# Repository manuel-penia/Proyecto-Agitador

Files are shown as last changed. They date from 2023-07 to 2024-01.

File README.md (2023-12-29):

# Agitador Magnético

En este proyecto se documenta la realización de un agitador magnético sencillo de bajo costo y con **componentes reutilizados** de computadoras viejas. Incluimos los componentes y circuitos asi como del software usado para controlar, mediante una placa Arduino, la velocidad de giro de un ventilador y la actuación sobre una pantalla de 7 segmentos que muestra un temporizador.

---

# Contenidos

1. [Motivación](#Motivación)
    1. [¿Agitadores magnéticos?](##¿Agitadoresmagnéticos?)
2. [Nuestro Agitador](#NuestroAgitador)
    1. [Uso](#uso)
    2. [Lista de Componentes](#lista-de-componentes)
    3. [Circuito](#circuito)
    4. [Software](#software)
    5. [Impresión 3D](#Impresión3D)
3. [Inspiración](#Inpiración)

---

# Motivación

<p align="justify"> Realizamos este proyecto con el fin de crear una sistema de fácil implementación para construir un agitador magnético que actualmente tienen precios altos y que sea funcional para el trabajo en el laboratorio.
 </p>

## ¿Agitadores magnéticos?

<p align="justify"> Los agitadores magnéticos se utilizan para la mezclar de soluciones químicas. Los agitadores comerciales consisten de una pequeña barra magnética recubierta por una capa de plástico y una placa debajo donde se encuentra un imán rotatorio a fin de crear un campo magnético que gire. Es muy frecuente que tenga un montaje de resistencias eléctricas a fin de generar calor necesario para calentar algunas soluciones químicas.</p>
___

# Nuestro Agitador

<p align="justify"> Para el diseño de nuestro agitador tuvimos en cuenta que debía tener la funcionalidad principal de hacer girar el buzo (para realizar el mezclado) y a su vez que tuviera un temporizador, con el cual pasado el tiempo seleccionado se apague el agitador. </p>

## Uso

<p align="justify"> Presionando el botón amarillo se elige la cantidad de tiempo deseada en el temporizador, con el botón rojo se da inicio al descuento de dicho tiempo. Se puede frenar el giro del ventilador presionando nuevamente el botón rojo. Una vez que arrancó el temporizador, mediante el giro del potenciómetro se controla la velocidad de giro del ventilador y por ende del buzo en la solución. Recomendamos aumentar gradualmente la velocidad de giro hasta la velocidad deseada. 
 </p>

## Lista de componentes

1. [Placa Arduino UNO](https://proyectoarduino.com/arduino-uno-r3/)
2. Entradas:
    1. [Potenciómetro](https://programarfacil.com/blog/arduino-blog/el-potenciometro-y-arduino/)
    2. [Botones](https://openwebinars.net/blog/tutorial-arduino-entradas-2-botones/) .
3. Salidas:

    1. Ventilador con PWM [AMD AFB 3300 rpm](https://ar.mouser.com/datasheet/2/632/AFB70x70x15mm-515820.pdf)
    2. [Display LCD](https://www.circuitbasics.com/arduino-7-segment-display-tutorial/).

4. Alimentación:

    1. Fuente de aliemntacion 12 V [Megalite SF120050](https://megalite.com.ar/data/Catalogo_Nielsen.pdf).

5. Otros accesorios:
    1. Cables Dupont Macho Hembra y Macho Macho de 20cm x **30**.

## Circuito

<p align="justify"> En cuanto al circuito, la fuente de alimentación se conecta a la placa Arduino mediante la entrada de 12V. El pin Vin redirecciona el voltaje de alimentación al ventilador. A traves del relay se conecta el cable Vin que conecta el ventilador. El controlador PWM del ventilador sale del pin 3 que tiene funcionalidad PWM. Por otro lado, la salida analógica del potenciómetro se conecta al Arduino por la entrada A2 y la alimentación es de 5V que proporciona el Arduino. El modulo Relay tiene su sistema de de alimentación de 5V con los pines de la placa y el cable sensor por la salida digital 8. Ademas cuenta con 2 botones en una configuración pull-down. Para esto se conecta una resistencia de 10 ohms en la salida GND de los botones. Todos estos componentes se conectan a los pines GND del Arduino. Finalmente el display LCD 16 x 2  se conectan las entradas analogicas A5 y A4 como indica la imagen, estas funcionan como comunicación, luego la alimentación es por 5V propio del arduino. Todos los componentes deben conectarse a tierra. </p>

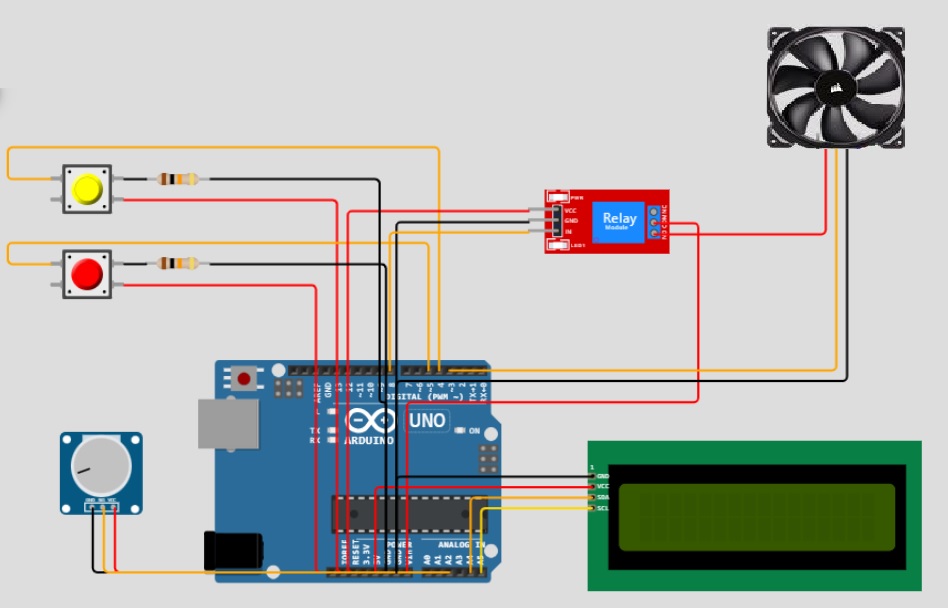
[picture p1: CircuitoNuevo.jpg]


## Software

El código utilizado se encuentra en el archivo [Codigo-Arduino.ino](https://github.com/manuel-penia/Proyecto-Agitador/blob/main/C%C3%B3digo-Arduino.ino)
Para simplificar la lectura y funcionamiento del codigo se realizo el siguiente diagrama explicativo. En donde, las variables azules son globales y las negras son locales.

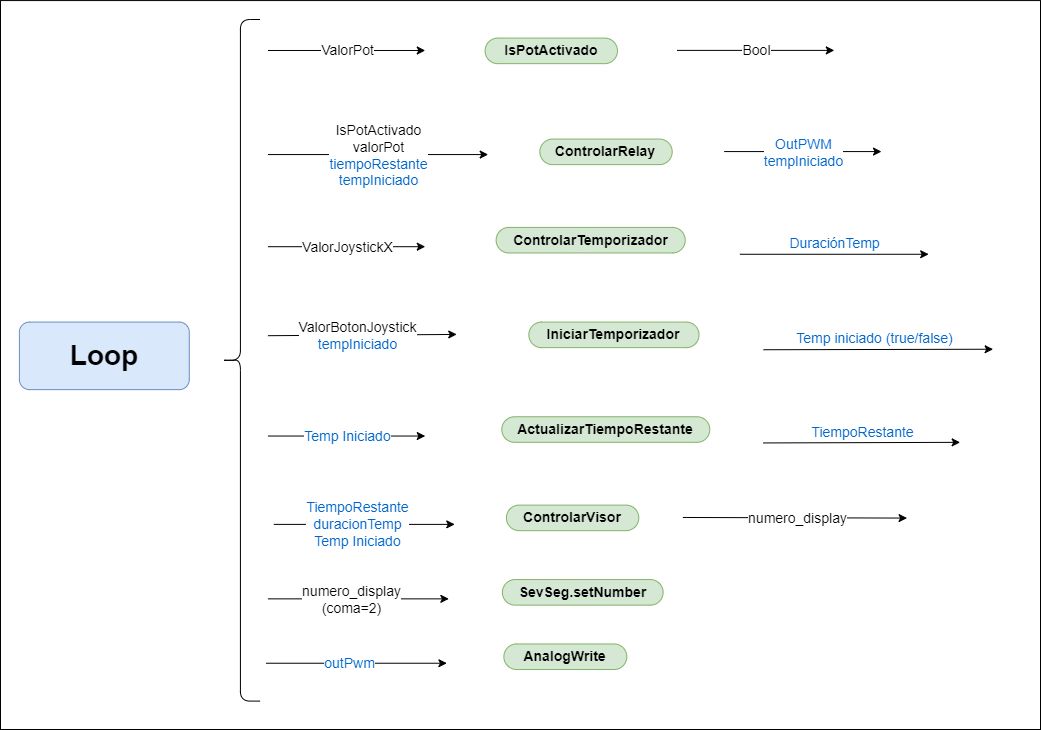
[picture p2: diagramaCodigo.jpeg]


## Impresión 3D

Se construyó un soporte en la plataforma online TinkerCad dispuesto en tres partes. El diseño consta de tres partes, la inferior, la intermedia y la superior. En la inferior hay espacios para atornillar la placa y el relé al suelo y contra una de las paredes se conectan los botones (Se construye una parte que funciona como traba), potenciometro y el visor LED. La intermedia se debe encastrar a la parte inferior y sobre ella se atornilla el ventilador con el imán pegado. La parte superior se desliza sobre las otras dos funcionando como tapa.
Para regular la fuerza de los imánes se construyó una plataforma circular que eleve el vaso precipitado a la distancia deseada.
También se contruyó el buzo que se introduce en la solución. Dentro del buzo se encuentran los imanes de neodimio. Todos los archivos stl se encuentran en esta [carpeta.](https://github.com/manuel-penia/Proyecto-Agitador/tree/main/IMPRESI%C3%93N)

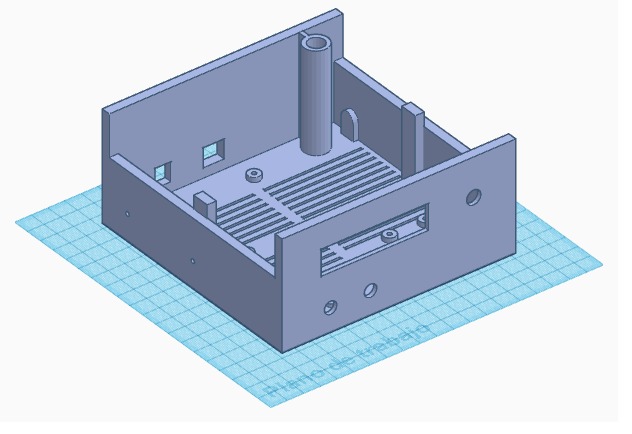
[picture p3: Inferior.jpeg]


# Inspiración

Hay proyectos de agitadores de los cuales nos inspiramos para realizar el proyecto, algunos no utilizan una placa Arduino y ninguno posee un temporizador.

+https://www.thingiverse.com/thing:1175415

+https://www.youtube.com/watch?v=muBcyEvqCYk&ab_channel=CambatronicsOnline

+https://forum.arduino.cc/t/controlar-ventilador-con-arduino/427074

+https://fdossena.com/?p=ArduinoFanControl/i.md

+https://www.youtube.com/watch?v=YBNEXWp-gf0

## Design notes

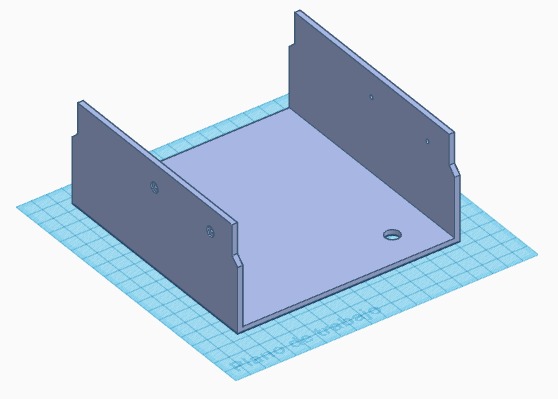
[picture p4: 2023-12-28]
Superior.jpeg

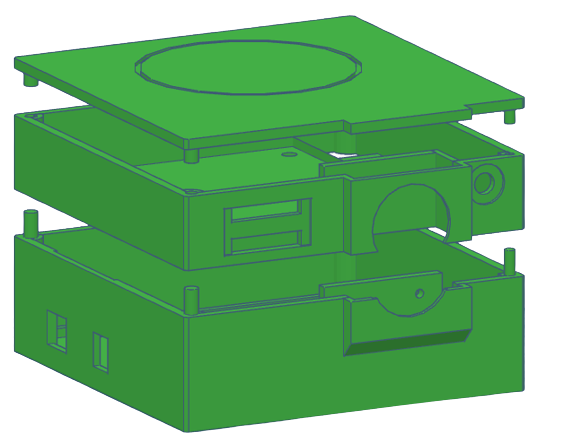
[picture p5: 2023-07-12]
desglose_impresion.png

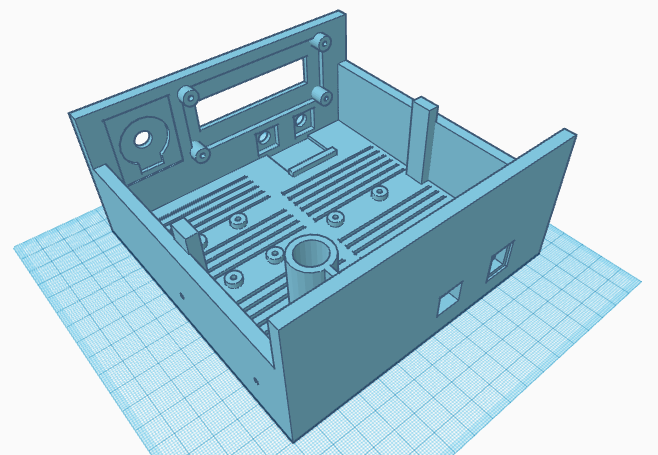
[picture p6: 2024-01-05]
BASE.png

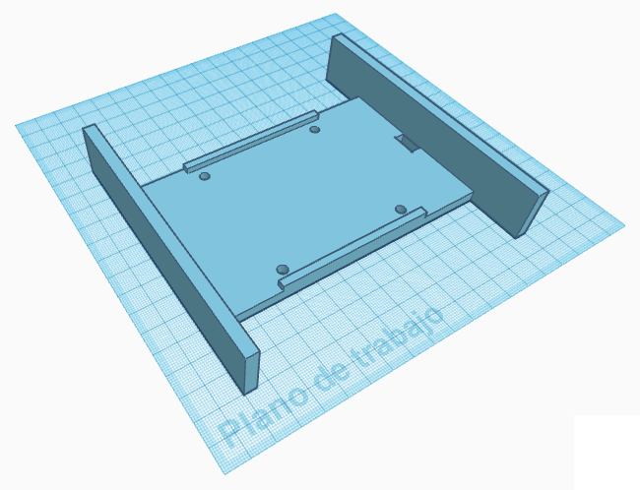
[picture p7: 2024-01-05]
COOLER.png

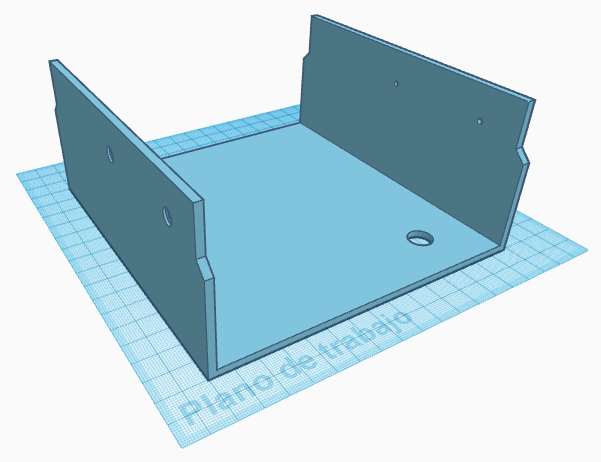
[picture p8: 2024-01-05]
TAPA.png

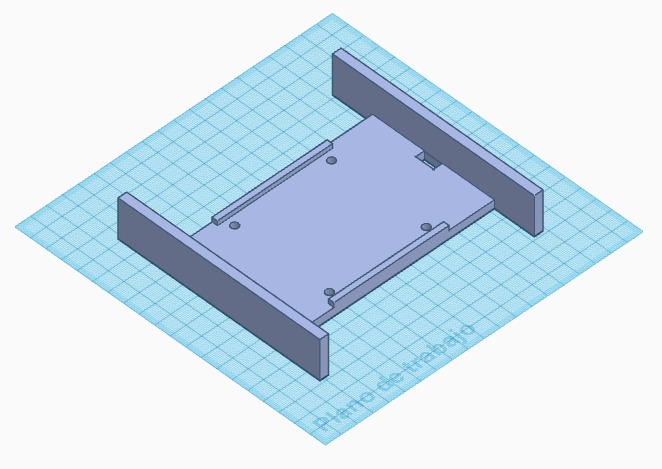
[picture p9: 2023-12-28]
Interno.jpeg

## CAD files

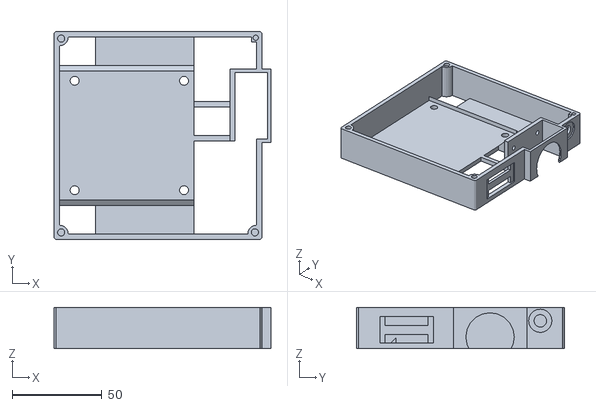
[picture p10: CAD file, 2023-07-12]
IMPRESIÓN/Intermedio.stl
121.0 x 116.0 x 23.0

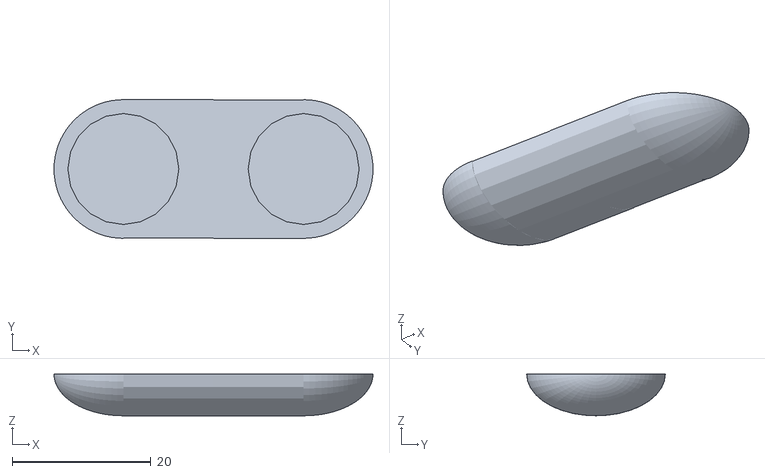
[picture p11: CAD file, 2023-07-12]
IMPRESIÓN/Buzo.stl
46.0 x 20.0 x 6.00

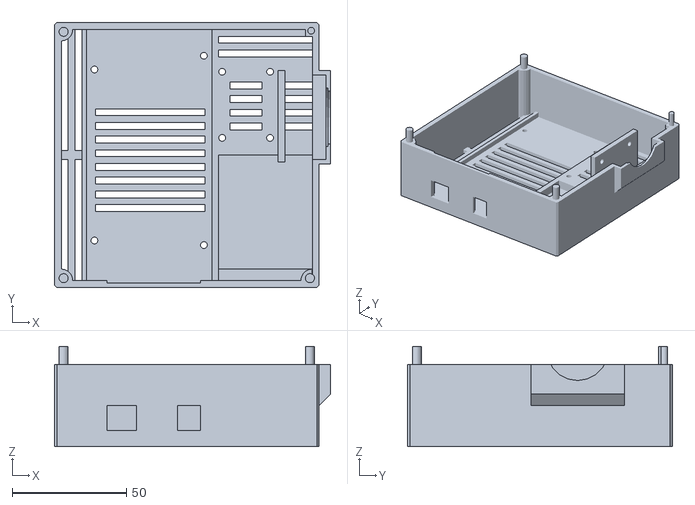
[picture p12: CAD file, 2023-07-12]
IMPRESIÓN/Base.stl
121.0 x 116.0 x 44.0

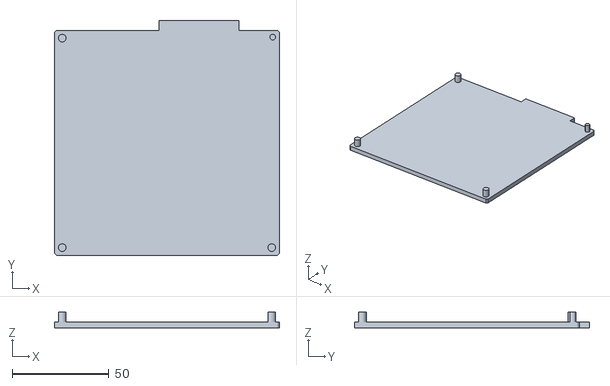
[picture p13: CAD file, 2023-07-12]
IMPRESIÓN/Tapa.stl
116.0 x 121.0 x 8.00

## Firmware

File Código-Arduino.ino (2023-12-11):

#include <LiquidCrystal_I2C.h>
#include <Wire.h> 

const int pinPot=A2;
const int pinControlRelay=8;
const int pinBotonTiempo=4;
const int pinBotonIniciar=5;
const int pinPWMVent=3;  //salidaPWM
LiquidCrystal_I2C lcd(0x27,16,2);

const int umbralMinimo=300; // Umbral mínimo para ajustar la salida del PWM y controlar la conexión/desconexión del voltaje de 12V.

int outPwm=0;  // Salida PWM (0-255) que regula el voltaje de entrada al ventilador y, por lo tanto, la velocidad.
int tiempoRestante = 0; // Tiempo restante en el temporizador.
bool temporizadorIniciado = false; // Estado del temporizador.
float duracionTemporizador = 0;  //Es el valor a setear en el temporizador en segundos.
long botonTiempoLastPressed = 0;

void setup() {
  pinMode(pinPot, INPUT);
  pinMode(pinControlRelay, OUTPUT);
  pinMode(pinBotonTiempo, INPUT);
  pinMode(pinBotonIniciar, INPUT);
  pinMode(pinPWMVent, OUTPUT);
  digitalWrite(pinControlRelay, HIGH);  // Inicialmente, mantener el relé apagado para no permitir la conexión del voltaje de 12V.

  // Inicializar el LCD
  lcd.init();
  
  //Encender la luz de fondo.
  lcd.backlight();
  
  Serial.begin(9600);
  Serial.println(outPwm);
}

bool IsPotActivado(int valorPot){
  if (valorPot < umbralMinimo) {  //umbralMínimo es una Constante Global.
    return false;
  } else {
    return true;
  }
}

void ControlarRelay(int valorPot, bool temporizadorIniciado){
  if (IsPotActivado(valorPot) && temporizadorIniciado) {
      digitalWrite(pinControlRelay, HIGH);  // Conectar el voltaje de 12V encendiendo el transistor.
      outPwm = map(valorPot, umbralMinimo, 1023, 0, 255);  // Mapear los valores del potenciómetro al rango del PWM (0 a 255 es el default).
      Serial.println(outPwm);
  } else {
      digitalWrite(pinControlRelay, LOW);  // Desconectar el voltaje de 12V apagando el relé.
  }
}

void ControlarTemporizador(){
  if (tiempoRestante <= 0) {
      temporizadorIniciado = false;  // Detener el temporizador cuando se agota el tiempo.
      tiempoRestante = 0;
    }
}

void aumentarTemporizador() {
  long tiempoActual = millis();
  if (tiempoActual - botonTiempoLastPressed >= 500) {
    botonTiempoLastPressed = tiempoActual;
    if (tiempoRestante == 0) {
      tiempoRestante += 30;
    } else {
      tiempoRestante *= 2;
    }
  }
}


void ActualizarTiempoRestante(){
  static unsigned long timer = millis(); //Guardamos la hora
  if (millis() - timer >= 1000) {
    timer += 1000;
    if (temporizadorIniciado) {
      tiempoRestante -= 1;
      lcd.clear();
    }
  }
}
void segundos_a_hh_mm_ss(int segundos, char* resultado) {
  int horas = segundos / 3600; // 1 hora = 3600 segundos
  int minutos = (segundos % 3600) / 60;
  int segundosRestantes = segundos % 60;

  // Formatear la cadena con el tiempo en formato HH:MM:SS
  sprintf(resultado, "%02d:%02d:%02d", horas, minutos, segundosRestantes);
}

int valorPot;
int valorBotonTiempo;
int valorBotonIniciar;
int numero_display;

void loop() {
  valorPot=analogRead(pinPot);
  valorBotonTiempo=digitalRead(pinBotonTiempo);
  valorBotonIniciar=digitalRead(pinBotonIniciar);

  if (temporizadorIniciado) {
    ControlarTemporizador();
    
    if (valorBotonIniciar == HIGH) {
      temporizadorIniciado = false;
      delay(500);
    }
    
  } else {
    if (valorBotonIniciar == HIGH) {
      temporizadorIniciado = true;
      delay(500);
    }
    if (valorBotonTiempo == HIGH) {
      aumentarTemporizador();
    }
  }
    
  ActualizarTiempoRestante();
  
  ControlarRelay(valorPot, temporizadorIniciado);
  

  lcd.setCursor(0, 0);
  lcd.print("Tiempo: ");
  
  lcd.setCursor(8, 0);
  char tiempo_formateado[9];
  segundos_a_hh_mm_ss(tiempoRestante, tiempo_formateado);
  lcd.print(tiempo_formateado);

  analogWrite(pinPWMVent, outPwm);
}

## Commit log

2023-06-28 Código-Arduino.ino
    Código de Arduino que controla el ventilador con un potenciómetro y un relay
2023-07-09 Código-Arduino.ino
2023-12-28 Delete Circuito.jpeg
    Circuito viejo no funciona
